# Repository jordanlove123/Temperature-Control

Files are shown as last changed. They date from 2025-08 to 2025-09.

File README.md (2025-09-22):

# Temperature Control
System for controlling temperature of an object to within 10 mK of a given setpoint.

DISCLAIMER: As is discussed below, some parts of the system will have to be designed by the user because they depend on the shape, size, and thermal mass of the object. This means that to a certain extent, performance is dependent on the user's design of these components, but I tried to include as many recommendations as possible for best practices.

## Setup

### Recommended installations
Before starting setup, there is software that is necessary to access some of the files in this repository:
* [Arduino IDE](https://www.arduino.cc/en/software/): Edit and upload Arduino code
* [KiCAD](https://www.kicad.org/download/): View and export PCB files
* [Prusa Slicer](https://www.prusa3d.com/page/prusaslicer_424/): Convert STL 3D models to gcode for a 3D printer
* [Realterm](https://sourceforge.net/projects/realterm/): Send serial commands and save serial data from Arduino to text file

These programs can all be downloaded for free.

### Manufacturing

#### Shield PCB
The PCB files can be found at [Manufacturing/Shield PCB](Manufacturing/ShieldPCB/). In order to get the manufacturing files, open the .kicad_pcb file and export according to what is necessary for your manufacturer of choice. If you don't have a manufacturer of choice, I recommend [JLCPCB](https://jlcpcb.com/). Once you have the board, assemble it according to the component labels in the .kicad_sch file. The complete list of necessary components can be found in the [bill of materials](Manufacturing/BOM.xlsx).

#### Container (optional)
If you have access to a 3D printer, I recommend printing the container found in [Manufacturing/Box](Manufacturing/Box). This can be done by opening the .stl files in Prusa Slicer and converting them to gcode:

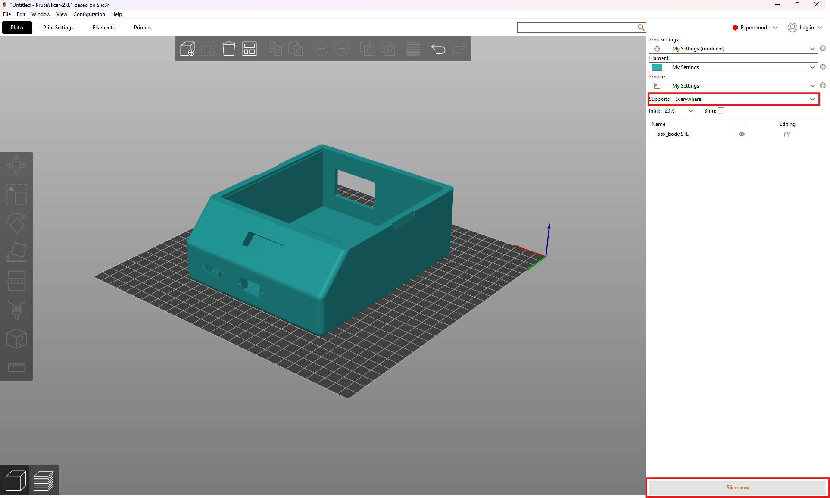
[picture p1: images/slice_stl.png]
Slice .stl file


Then export the gcode file and give it to your 3D printer:

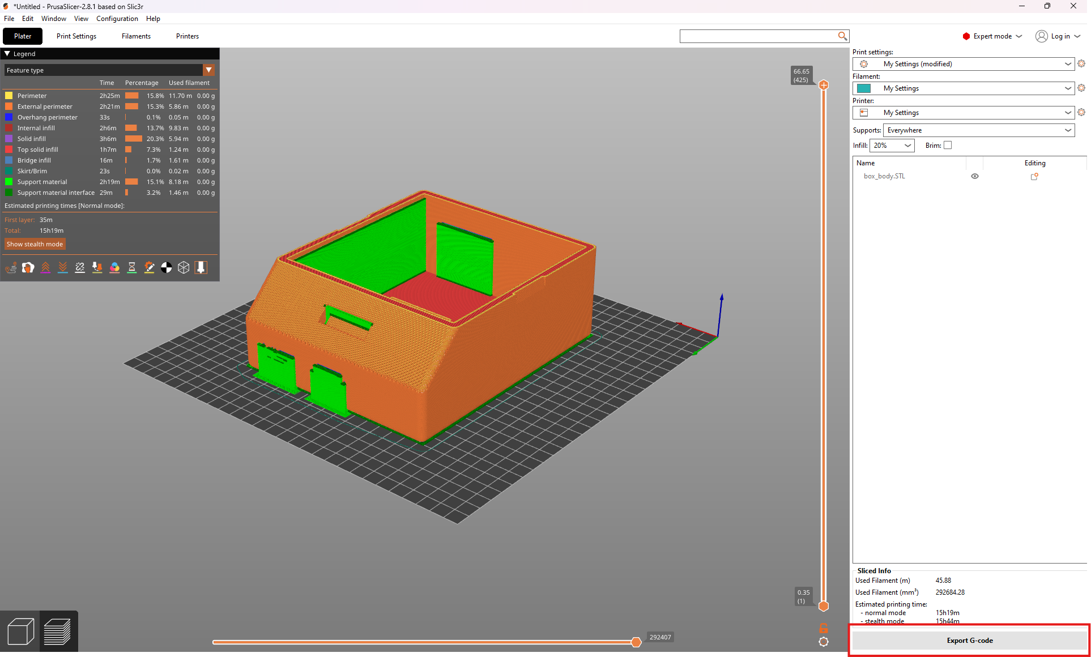
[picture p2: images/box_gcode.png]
Export gcode


#### Temperature Probe
This system uses two temperature sensors: one for the feedback loop that controls the temperature in addition to a heater, and one for independent monitoring of the temperature with a sensor outside the feedback loop. Because the configuration of these sensors and the heater will depend on the form factor of the object being temperature controlled, there is no case for them in this repository, but there are requirements for how it is built. The temperature sensors should be two 10k thermistors in a voltage divider as shown below:

<div align="center">
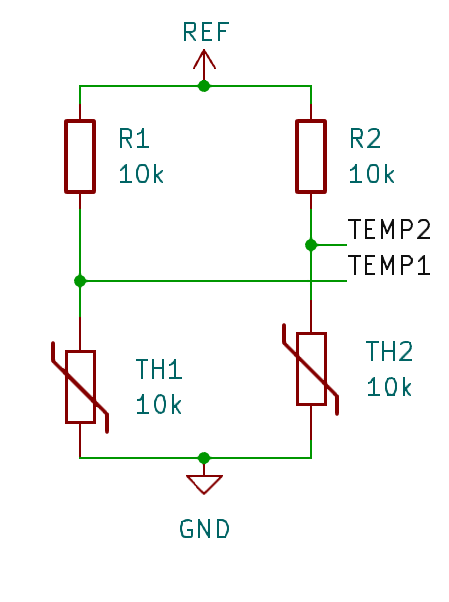
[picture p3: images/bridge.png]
    
</div>

TEMP1 and TEMP2 are the two signal cables that will be connected to IN1 and IN2 on the shield, REF comes from the REF pin on the shield and is generated by the on-board 2.5V voltage regulator, and GND comes from one of the GND pins on the shield. Additionally, a heating resistor connected to the R6 pin header should be placed near the object being temperature controlled. If you're using the optional container, all of the wires in your case should be connected to a d-sub 9 connector so they can be plugged into the container. Some additional recommendations for configuration of the probe:

* Try to thermally isolate the sensor-heater-object system as best as you can with the case that you build. This will have the largest effect on the performance of the system.
* Place the temperature sensors far from the heater. This will ensure that you're measuring the actual temperature of the object, not just the temperature of the heater.
* Don't place the sensors too close to each other so you can see on the independent sensor if the object is being heated unevenly.
* Try to match the resistors in the voltage dividers as best as possible. This will ensure that the voltage you measure on both dividers is the same as long as the temperature is the same.

Because the performance is largely dependent on the probe setup, there are no guarantees that you will get mK-level stability if it isn't good enough. However, below you will find tools to assess the performance and potential flaws of your setup so you can iterate your design until it is good enough.

### Assembly
Connecting the shield PCB to the Arduino is very simple: just align the pins coming from the underside of the PCB with the input pins of the Arduino and connect them directly so the PCB is sitting on top of the Arduino. There should be an exact one-to-one match between PCB pins and Arduino pins. If you're using the optional container, use the following images as a reference to place the components within it correctly.

Box front:

<div align="center">
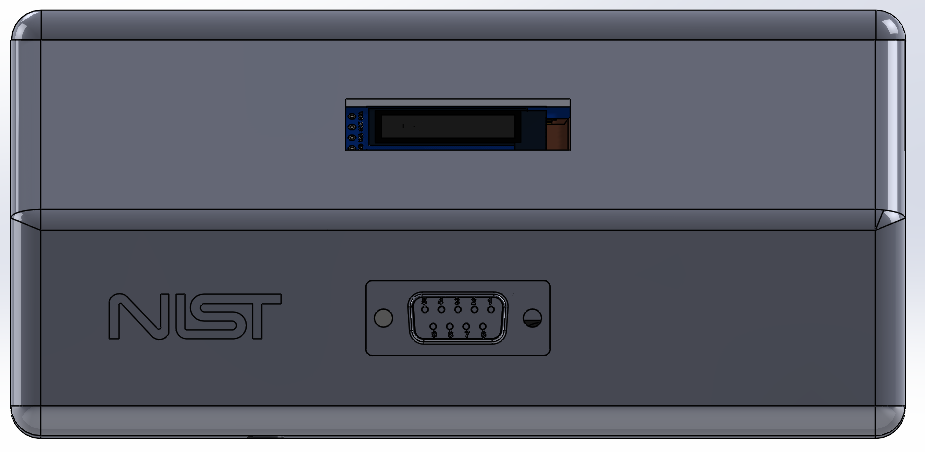
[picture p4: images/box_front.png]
    
</div>

Box back:

<div align="center">
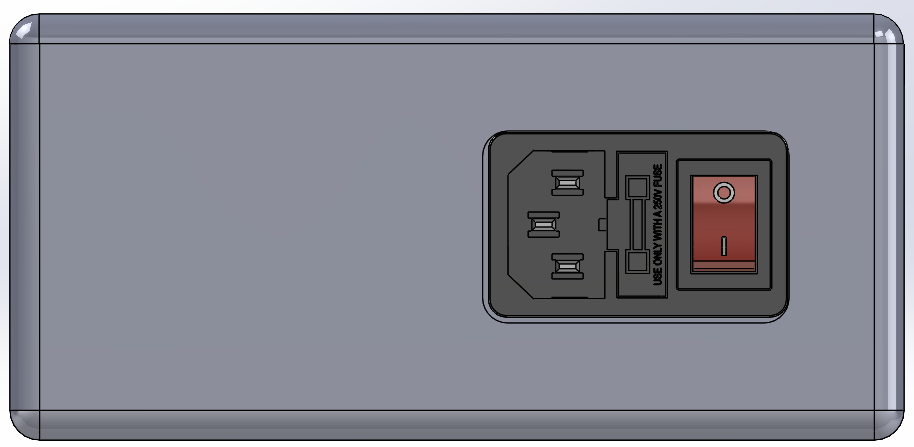
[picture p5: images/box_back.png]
    
</div>

Box top:

<div align="center">
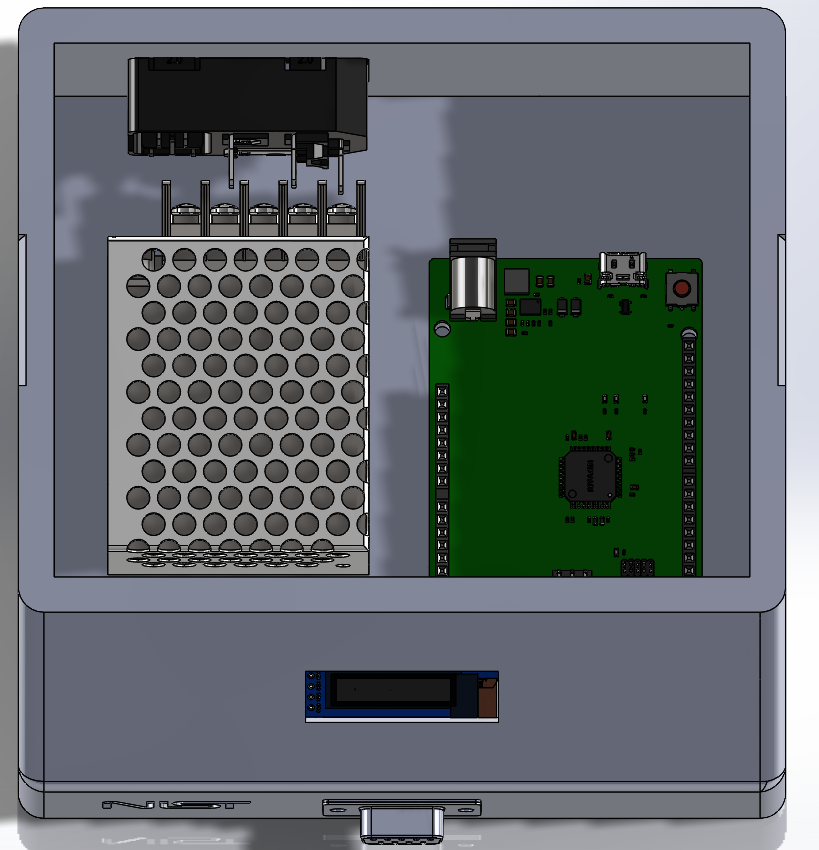
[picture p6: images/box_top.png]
    
</div>

Use the following wiring diagram to make the necessary connections:

<div align="center">
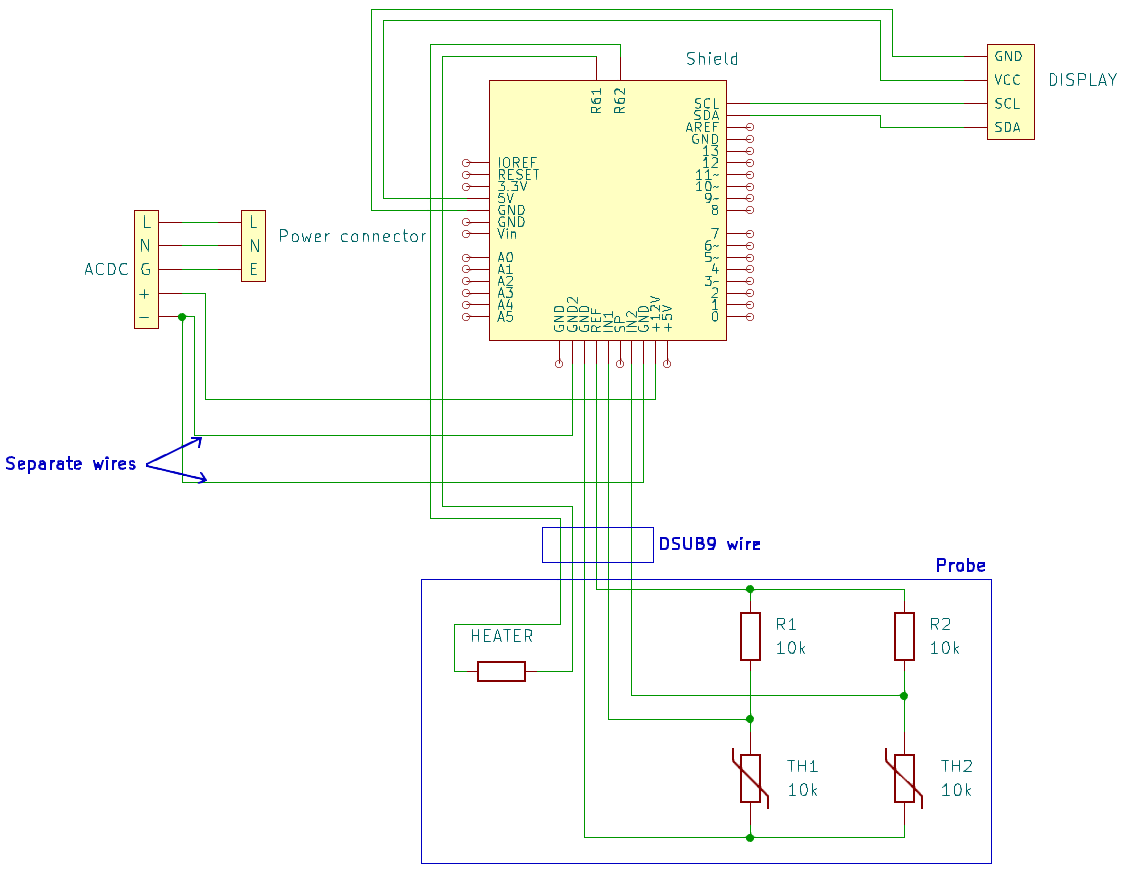
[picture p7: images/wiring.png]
    
</div>

WARNING: THE WALL PLUG CARRIES HIGH VOLTAGES WHEN CONNECTED. BE VERY CAUTIOUS WHEN WORKING WITH POWER CABLES AND DO NOT PLUG IN THE BOX UNTIL ALL THESE CABLES ARE SHRINK WRAPPED AND THERE IS NO EXPOSED METAL. PLUGGING IN WITHOUT TAKING THE CORRECT PRECAUTIONS COULD CAUSE HARM.

### Code
The Arduino code makes use of two custom libraries: AD7190 for interfacing with the ADC on the shield and PID for handling the feedback loop of the system. These two folders can be found in [Code/Libraries](Code/Libraries) and can be installed using the following steps:

* Save both folders as a zip file
* Open the Arduino IDE and select Sketch > Include Library > Add .ZIP Library
* Navigate to the location where your libraries are saved and select them

The code to be uploaded to the Arduino is found in [Code/Arduino](Code/Arduino)

## Usage

### Serial commands
The Arduino accepts a variety of commands to interface with the PID system, which are summarized in the table below:
| Command          | Arguments accepted             | Description                                                                                                 |
|:-----------------|:-------------------------------|:------------------------------------------------------------------------------------------------------------|
| p \[arg1\]       | arg1: double > 0               | Change the K<sub>p</sub> parameter of the PID system                                                        |
| i \[arg1\]       | arg1: double > 0               | Change the K<sub>i</sub> parameter of the PID system                                                        |
| d \[arg1\]       | arg1: double > 0               | Change the K<sub>d</sub> parameter of the PID system                                                        |
| heat \[arg1\]    | arg1: 0 or 1                   | Turn heater off (0) or on (1)<sup>1</sup>                                                                   |
| setp \[arg1\]    | arg1: double < 29              | Change the setpoint of the PID system                                                                       |
| verbose \[arg1\] | arg1: 0 or 1                   | Output control stats to serial port (see [Serial output](#serial-output))                                   |
| rstime           | none                           | Restart the timestamp at 0                                                                                  |
| sint \[arg1\]    | arg1: double                   | Set the integral term to a custom value<sup>2</sup>                                                         |
| save             | none                           | Save the current K<sub>p</sub>, K<sub>i</sub>, K<sub>d</sub>, and setpoint to EEPROM<sup>3</sup>            |

<sup>1</sup> This is implemented in practice by multiplying the heater output by arg1, so passing any other number will have the effect of changing the gain of the entire system

<sup>2</sup> Due to the anti-windup, if |arg1| > 10, it will be set to either -10 or +10

<sup>3</sup> When an Arduio program is running, variables are stored in program memory which is volatile, meaning it is lost when the Arduino loses power. However, the Arduino also has a non-volatile form of data storage called EEPROM, so if you want to move your controller and disconnect power you won't lose the parameters you found during tuning. This memory has a limited number of write cycles though, so use this command sparingly.

Due to an unknown bug in the Arduino code, commands need to be sent multiple times in quick succession in order for them to be properly received.

### Serial output

When verbose is set to true, data is output to the serial port in the following format:

**Timestamp &nbsp;&nbsp;&nbsp; Temperature voltage &nbsp;&nbsp;&nbsp; Independent sensor reading &nbsp;&nbsp;&nbsp; Error voltage &nbsp;&nbsp;&nbsp; Proportional term &nbsp;&nbsp;&nbsp; Integral term &nbsp;&nbsp;&nbsp; Derivative term &nbsp;&nbsp;&nbsp; Output power &nbsp;&nbsp;&nbsp; Output voltage to heater circuit**

### Tuning
DISCLAIMER: This is not necessarily the optimal tuning method, but just the one that I found works best for me. If you have another method that you prefer and you know it works better, go ahead and use it. This is just for a beginner to get a feel for tuning. However, I have found that some common tuning methods don't work very well, possibly because of some of the non-linearities in the system.

NOTE: There is a [jupyter notebook](Code/Data%20Analysis/data_analysis.ipynb) in Code/Data Analysis that can be used to help with tuning. If you would like to use your own analysis techniques, it is not required to use this notebook, however if you have your own analysis techniques in addition to those found in the notebook, you probably don't need this section anyway.

The notebook has 3 main cells that will be useful. The first one, third from the top, will just take your data and plot everything from the serial output on it's own axis for the entire dataset. This can be used to look at your data wholistically and to analyze long term stability. The next cell from the top will plot the last 150 seconds of data, and updates every second. This can be used if you want to see live-updating data and catch any large errors without having to wait to see everything at once. The last one is the PSA spectrum of the P, I, and D terms of the controller and the temperature data. This essentially shows you how much of each frequency is contained in the data, which is useful for reasons explained below.

#### Step response
When tuning, you will want to look at the step response of your system, which is just how it responds to an instantaneous change in the setpoint (In this case, moving it up). Do this by turning off the heater, waiting for the temperature to return to room temperature, then sending the command "sint 0" and turning the heater back on. The step response will be the temperature graph after turning the heat back on.

#### Recognizing issues
Once you get to the point of tuning the parameters of the system, you want to make sure the probe setup is good enough, because otherwise you're limited by the quality of your setup instead of the accuracy of the parameters. The main issue that you will run into with the probe setup is insufficient thermal isolation, which means surrounding air temperature is being factored into your measurement. Generally, the object being temperature controlled will have a much larger thermal mass than the surrounding air, so watch for large, quick changes in temperature. A normal time period for a temperature change depends on your thermal mass, but will typically be on the order of a couple minutes. If you see relatively large temperature changes happening in a matter of seconds, it's probably a probe issue rather than a parameter issue.

#### Step 0: The basics
Before starting, a general overview of PID. PID stands for proportional, integral, derivative, and controls a system using exactly those things. It takes as input the error between the setpoint and the actual temperature and outputs the negative sum of the integral of the error, derivative of the error, and exact error all scaled by constants, called the gains. The proportional term just pushes the temperature towards the setpoint. This might be enough in some cases, but think about what would happen if the error were 0 and the temperature was above room temperature. A controller with only the proportional term would not be doing anything to keep the temperature above room temperature because K*0 = 0 so it would output 0. This means any controller with only the proportional term will have some steady state error. This is where the integral term comes in. If there is any steady state error, the integral term will accumulate over time, pushing the temperature towards the setpoint. The speed that it accumulates is dictated by the integral gain. Notably, too high of a proportional gain or integral gain will cause oscillations, which are not what we want. This is where the derivative term comes in. It can be thought of as predicting the future; if the derivative is positive, the temperature will probably go up, and so the derivative term preemptively reduces the output power to reduce this change. Such a term will provide damping of oscillations, and that is its job.

#### Step 1: Picking a setpoint
Before doing any tuning, figure out the ambient temperature of the object being temperature controlled using the system. The system guarantees high precision, but not high accuracy, so doing this will give you a frame of reference for what the temperature actually is. Once you've done this, set the setpoint. It can be whatever you want but is bounded on both sides by two factors: the bottom end is about 2-3 <sup>o</sup>C above room temperature since the system has no cooler so ambient temperature is used to cool it, and the upper end is limited by your heater's power output. This depends on the resistance of the heater and the input voltage that you use (12V if you use the optional container with no modifications).

#### Step 2: Finding proportional gain
The next step after setting the setpoint is to find K<sub>p</sub>, the proportional gain of the system. To find the proportional gain, just pick a number to start. If the step response goes past the setpoint, reduce it by half until it doesn't. Then, slowly turn it up and watch the step response each time you change it. Once it is settling close to the setpoint, but slightly below, move on to step 3.

#### Step 3: Finding integral gain
First, cut your proportional gain in half, and then pick a number for your integral gain. It will probably be much smaller than the proportional gain you found. If the oscillations are centered above the setpoint while it settles, turn the integral gain down. If below, do the opposite. Once the oscillations are centered approximately at the setpoint, move on to the next step.

#### Step 4: Finding derivative gain
This step is pretty simple, just turn up the derivative gain until the oscillations are damped as much as is necessary for your purposes. The higher it is, the more damped they will be. If your derivative gain gets too high, the integral term might accumulate more than it was before because the derivative term slows the original ascent to the setpoint, so you'll need to turn down the integral gain slightly. Once you've finished finding the parameters, a good step response will look something like this:

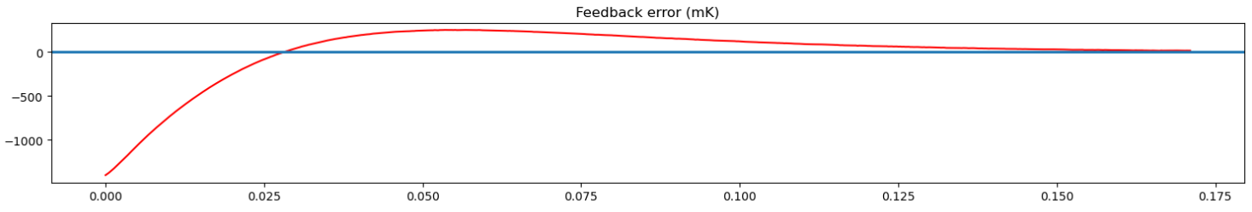
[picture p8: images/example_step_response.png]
Example step response


#### Step 5: Fine tuning the parameters
The above steps help with the original settling to the setpoint, but in order to get the best steady state performance, the parameters need to be tuned a little more. To do this, take about 12 hours of data after the temperature has settled and look at the PSA spectrum. An ideal spectrum will look like this:

<div align="center">
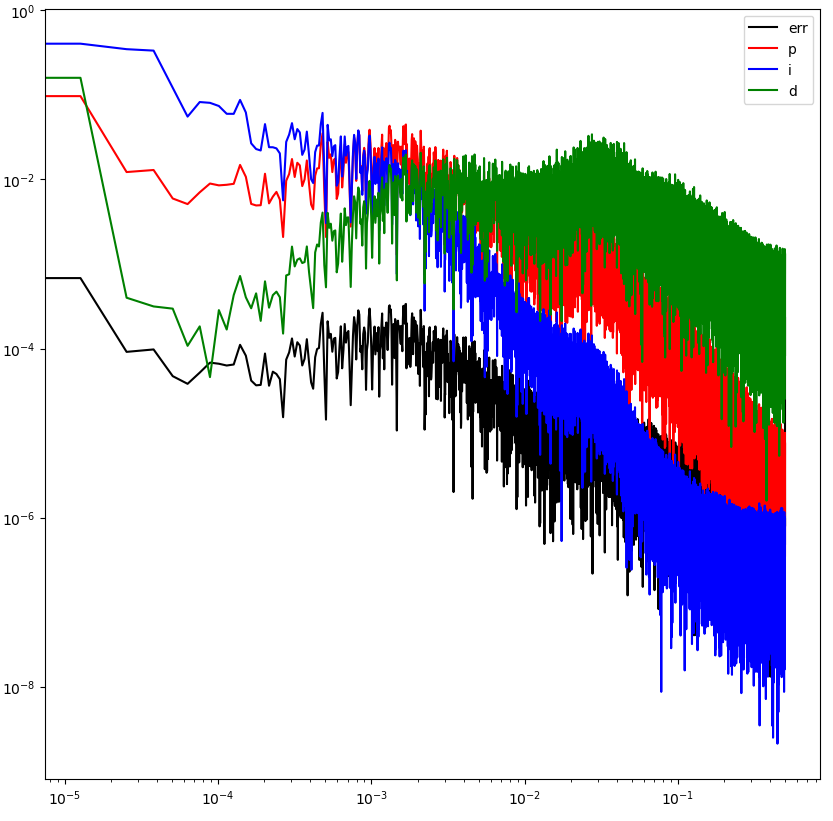
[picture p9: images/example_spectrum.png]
    
</div>

Note the integral term is the strongest at lower frequencies, then the proportional term takes over in the middle frequencies, and finally the derivative term takes over at high frequencies. It will also have two points where all terms will start to roll off: one is the natural frequency of your system; the temperature can't change any faster than that, and the other is due to a filter in the feedback loop. Just ignore these and look at the general shape. If the shape doesn't look like this, you can move each term up by multiplying it by a scaling factor, and move it down by dividing by a scaling factor. Scale the parameters appropriately and they should then be optimal.

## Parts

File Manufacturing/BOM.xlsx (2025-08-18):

Item | Digikey part number | Price | Quantity | Total Price | Optional?
Shield header kit | 1568-11417-ND | $2.75 | 1 | $2.75 | n
Fuse | 283-3263-ND | $0.91 | 1 | $0.91 | y
Schottky Diode | 1N5819HW-FDICT-ND | $0.23 | 1 | $0.23 | n
Inductor 330u | 495-B82432C1334K000CT-ND | $5.86 | 1 | $5.86 | n
Capacitor 330u | 478-APA0609331M010RCT-ND | $0.54 | 1 | $0.54 | n
Buck Converter | LM2575D2T-5R4GOSCT-ND | $17.92 | 1 | $17.92 | n
2 pin header | 952-2262-ND | $0.79 | 1 | $0.79 | n
Resistor 1k | 541-1.00KCCT-ND | $0.10 | 4 | $0.40 | n
Resistor 10k | RMCF0805FT10K0CT-ND | $0.10 | 1 | $0.10 | n
Resistor 10 | P10.0CCT-ND | $0.11 | 1 | $0.11 | n
Capacitor 1u | 1276-1029-1-ND | $0.08 | 5 | $0.40 | n
Resistor 5k | 541-CRCW08055K00FKTACT-ND | $0.11 | 1 | $0.11 | n
MMBT3904 Transistor | 4878-MMBT3904CT-ND | $0.11 | 1 | $0.11 | n
2.5 Vref | 296-39165-1-ND | $3.54 | 1 | $3.54 | n
AD7190 ADC | 505-AD7190BRUZ-REELCT-ND | $18.14 | 1 | $18.14 | n
Arduino uno r4 minima | 1050-ABX00080-ND | $20.00 | 1 | $20.00 | n
D-sub 9 connector | AE11063-ND | $0.52 | 2 | $1.04 | y
D-sub 9 cable | 116-30-9506-99-ND | $4.71 | 1 | $4.71 | y
Power cable | TL870-ND | $12.56 | 1 | $12.56 | y
ACDC converter | 1866-4128-ND | $8.60 | 1 | $8.60 | y
Jumper wires | 4526-KIT-ZW-20X3-ND | $14.80 | 1 | $14.80 | n
Power receptacle | 2057-IEC-GS-1-100-ND | $5.31 | 1 | $5.31 | y
Thermistor | 317-1258-ND | $0.32 | 2 | $0.64 | n
THT resistor 10k | CF14JT10K0CT-ND | $0.10 | 2 | $0.20 | n
Heating resistor | A129453CT-ND | $0.56 | 1 | $0.56 | n
OLED display* | etsy (https://www.etsy.com/listing/1593848368/128x32-oled-lcd-display-ssd1306-driver?gpla=1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) | $6.99 | 1 | $6.99 | y
PCB* | jlcpcb (https://jlcpcb.com/) | $20.00 | 1 | $20.00 | n
 |  |  | Total | $147.32
*Item not on digikey |  |  | Total without optional | $107.20

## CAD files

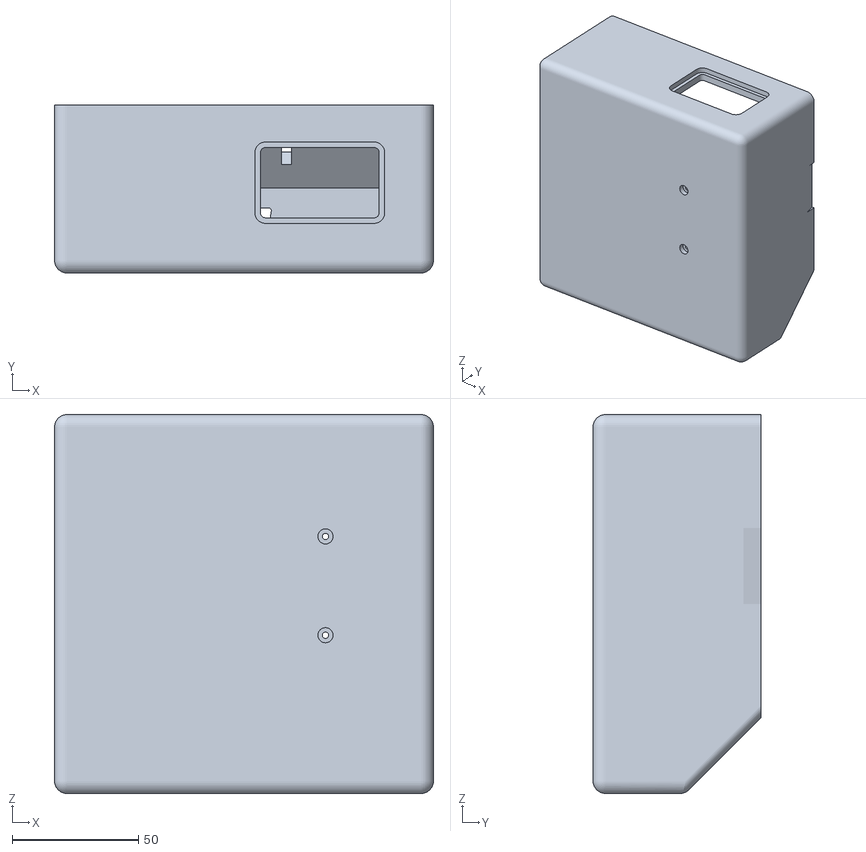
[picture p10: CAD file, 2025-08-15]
Manufacturing/Box/box_body.STL
150.0 x 66.5 x 150.0

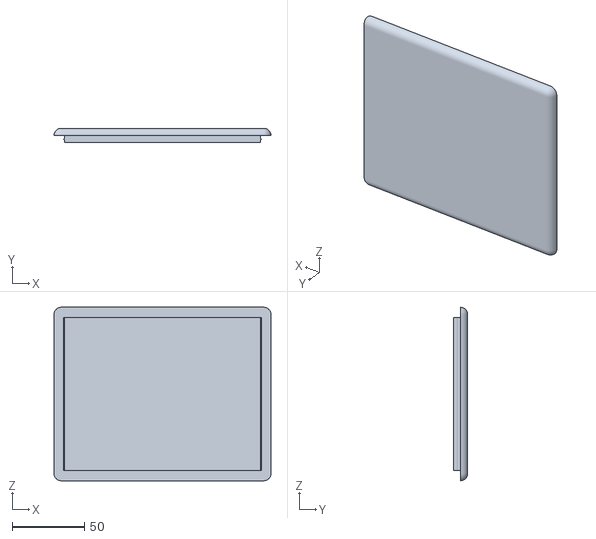
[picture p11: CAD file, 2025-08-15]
Manufacturing/Box/box_top.STL
150.0 x 10.0 x 120.0

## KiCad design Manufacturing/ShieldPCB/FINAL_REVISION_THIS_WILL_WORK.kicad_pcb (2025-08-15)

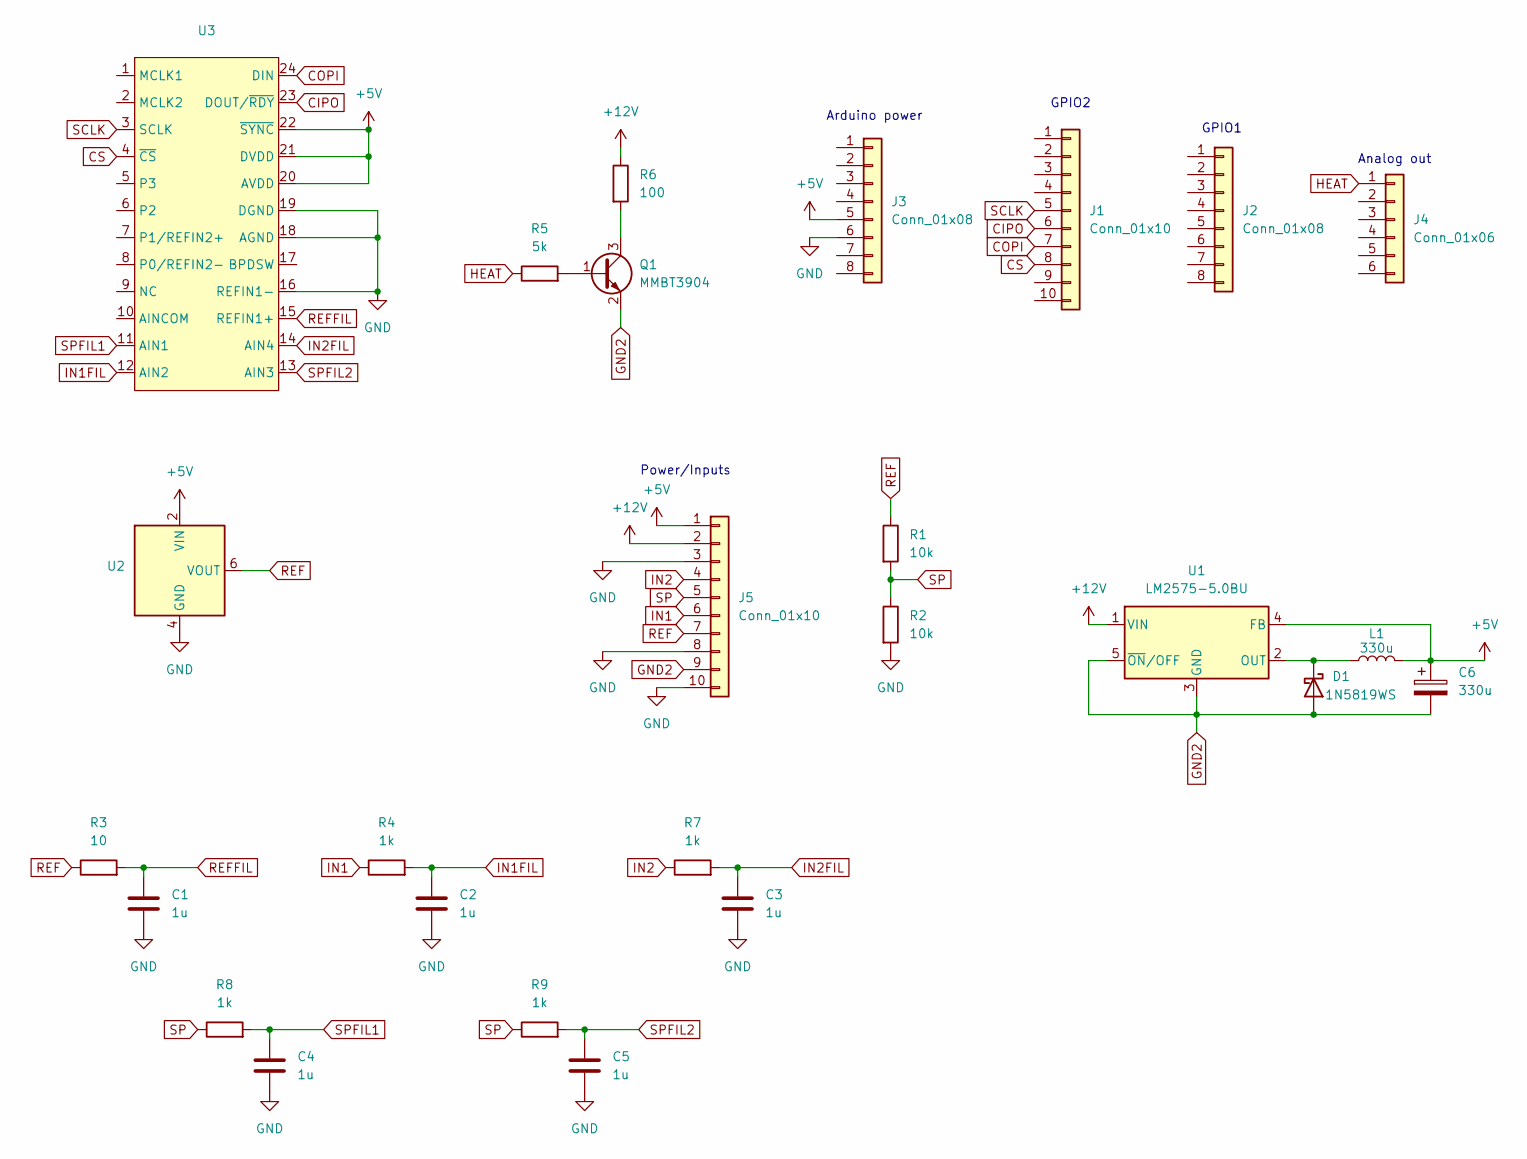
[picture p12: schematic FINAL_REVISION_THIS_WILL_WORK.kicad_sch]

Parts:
C1, C2, C3, C4, C5: 1u; C_0805_2012Metric
C6: 330u; C_Elec_6.3x7.7
D1: 1N5819WS; D_SOD-123
J1: Conn_01x10; PinSocket_1x10_P2.54mm_Vertical
J2, J3: Conn_01x08; PinSocket_1x08_P2.54mm_Vertical
J4: Conn_01x06; PinSocket_1x06_P2.54mm_Vertical
J5: Conn_01x10; PinHeader_1x10_P2.54mm_Vertical
L1: 330u; L_1812_4532Metric
Q1: MMBT3904; SOT-23
R1, R2: 10k; R_0805_2012Metric
R3: 10; R_0805_2012Metric
R4, R7, R8, R9: 1k; R_0805_2012Metric
R5: 5k; R_0805_2012Metric
R6: 100; PinHeader_1x02_P2.54mm_Vertical
U1: LM2575-5.0BU; TO-263-5_TabPin3
U2: SOIC-8_3.9x4.9mm_P1.27mm
U3: TSSOP-24_4.4x7.8mm_P0.65mm

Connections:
+5V: C6.1, J3.5, J5.1, L1.2, U1.4 (FB), U2.2 (VIN), U3.20 (AVDD), U3.21 (DVDD), U3.22 (~SYNC)
+12V: J5.2, R6.1, U1.1 (VIN)
CIPO: J1.6, U3.23 (DOUT/~RDY)
COPI: J1.7, U3.24 (DIN)
CS: J1.8, U3.4 (~CS)
GND: C1.2, C2.2, C3.2, C4.2, C5.2, J3.6, J5.3, J5.8, J5.10, R2.2, U2.4 (GND), U3.16 (REFIN1-), U3.18 (AGND), U3.19 (DGND)
GND2: C6.2, D1.2 (A), J5.9, Q1.2 (E), U1.3 (GND), U1.5 (~ON/OFF)
HEAT: J4.1, R5.1
IN1: J5.6, R4.1
IN1FIL: C2.1, R4.2, U3.12 (AIN2)
IN2: J5.4, R7.1
IN2FIL: C3.1, R7.2, U3.14 (AIN4)
unnamed: D1.1 (K), L1.1, U1.2 (OUT)
unnamed: Q1.1 (B), R5.2
unnamed: Q1.3 (C), R6.2
REF: J5.7, R1.1, R3.1, U2.6 (VOUT)
REFFIL: C1.1, R3.2, U3.15 (REFIN1+)
SCLK: J1.5, U3.3 (SCLK)
SP: J5.5, R1.2, R2.1, R8.1, R9.1
SPFIL1: C4.1, R8.2, U3.11 (AIN1)
SPFIL2: C5.1, R9.2, U3.13 (AIN3)

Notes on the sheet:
Arduino power
GPIO2
GPIO1
Analog out
Power/Inputs

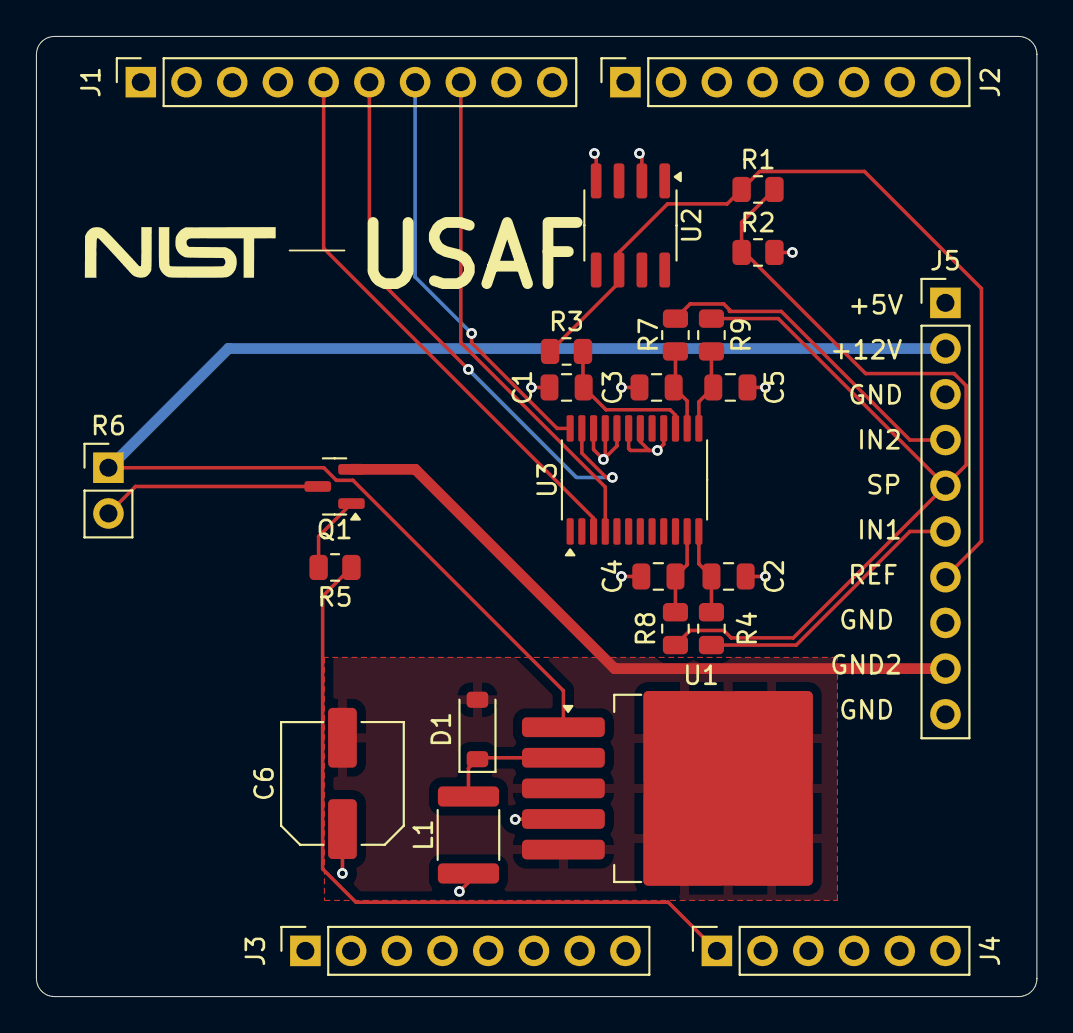
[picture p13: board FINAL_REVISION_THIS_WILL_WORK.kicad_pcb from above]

Board: 4 copper layers, 55.6 x 53.3 mm, 26 parts (0 on the bottom side), 21 nets.

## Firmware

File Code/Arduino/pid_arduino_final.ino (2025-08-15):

#include <SPI.h>
#include <Wire.h>
#include <Adafruit_GFX.h>
#include <Adafruit_SSD1306.h>
#include <AD7190.h>
#include <PID.h>
#include <math.h>
#include <EEPROM.h>

#define CS 10

#define SCREEN_WIDTH 128 // OLED display width, in pixels
#define SCREEN_HEIGHT 32 // OLED display height, in pixels
#define OLED_RESET     -1 // Reset pin # (or -1 if sharing Arduino reset pin)
#define SCREEN_ADDRESS 0x3C ///< See datasheet for Address; 0x3D for 128x64, 0x3C for 128x32
Adafruit_SSD1306 display(SCREEN_WIDTH, SCREEN_HEIGHT, &Wire, OLED_RESET);

// Display data
byte curr_ind = 0;
byte low[128];
byte high[128];
double max_candidate = -4;
double min_candidate = 4;

AD7190 ad7190(2.495);
//      130, 0.685, 5400
PID pid(130, 0.685, 5400, 0.00825, 120, true);
String c;
String in;
char buf1[16];
char buf2[16];
const double A = 0.001125308852122;
const double B = 0.000234711863267;
const double C = 0.000000085663516;
double vcc = 2.5;
int count = 0;
double sp_off = -0.05;
double last_params[4] = {0, 0, 0, 0};
double params_buf[4];

void double_to_eeprom(double d, int start_addr) {
  double *d_ptr = &d;
  long long d_int = *((long long*) d_ptr);
  byte temp;
  for (int i = 7; i >= 0; i--) {
    temp = (d_int >> (i*8)) & 0xFF;
    EEPROM.write(start_addr + 7-i, temp);
  }
}

double double_from_eeprom(int start_addr) {
  long long buf = 0;
  for (int i = 0; i < 8; i++) {
    long long temp = EEPROM.read(start_addr + i);
    buf |= temp << (7-i)*8;
  }
  long long *buf_ptr = &buf;
  double d = *((double*) buf_ptr);
  return d;
}

void load_params(double *buf) {
  // [sp, p, i, d]
  // !!!! Can cause buffer overflow if len(buf) < 4, don't do that !!!!
  for (int i = 0; i < 4; i++) {
    double temp = double_from_eeprom(8*i);
    if (isnan(temp) && i == 0) {
      temp = 27.5;
    }
    else if (isnan(temp)) {
      temp = 1;
    }
    buf[i] = temp;
  }
}

void save_params(double *params) {
  // !!!! len(params) must be 4 for correct operation !!!!
  for (int i = 0; i < 4; i++) {
    if (last_params[i] != params[i]) {
      last_params[i] = params[i];
      double_to_eeprom(params[i], 8*i);
    }
  }
}

double t_to_r(double T) {
  double x = 1/C*(A-1/(T+273.15));
  double y = sqrt(pow(B/(3*C), 3) + pow(x/2, 2));
  return exp(cbrt(y-x/2) - cbrt(y+x/2));
}

double r_to_v(double R) {
  return vcc * R / (10000 + R);
}

void updateDisplay(byte *low, byte *high, int curr_ind) {
  display.clearDisplay();
  int start = (curr_ind + 1) % 128;
  for (int i = 0; i < 128; i++) {
    for (int j = low[(i + start) % 128]; j <= high[(i + start) % 128]; j++) {
      display.drawPixel(i, j, SSD1306_WHITE);
    }
  }
  display.display();
}

void updateParams() {
  c = Serial.readStringUntil(' ');
  in = Serial.readStringUntil('\n');
  if (c != NULL && in != NULL) {
    c.toCharArray(buf1, 16);
    in.toCharArray(buf2, 16);
    int setting = atof(buf2);
    if (strcmp(buf1, "p") == 0) {
      pid.K_p = setting;
      params_buf[1] = setting;
    }
    else if (strcmp(buf1, "i") == 0) {
      pid.K_i = setting;
      params_buf[2] = setting;
    }
    else if (strcmp(buf1, "d") == 0) {
      pid.K_d = setting;
      params_buf[3] = setting;
    }
    else if (strcmp(buf1, "heat") == 0) {
      pid.heat = setting;
    }
    else if (strcmp(buf1, "setp") == 0) {
      sp_off = r_to_v(t_to_r(setting)) - 1.181;
      params_buf[0] = setting;
    }
    else if (strcmp(buf1, "verbose") == 0) {
      pid.verbose = setting;
    }
    else if (strcmp(buf1, "sint") == 0) {
      pid.set_integral(setting);
    }
  }
  else if (in != NULL) {
    in.toCharArray(buf1, 16);
    if (strcmp(buf1, "rstime") == 0) {
      pid.set_start_time();
    }
    else if (strcmp(buf1, "save") == 0) {
      save_params(params_buf);
    }
  }
}

void setup()
{
  Serial.begin(9600);
  analogWriteResolution(12);
  Serial.setTimeout(2);
  display.begin(SSD1306_SWITCHCAPVCC, SCREEN_ADDRESS);

  // Select ADC
  pinMode(CS, OUTPUT);
  digitalWrite(CS, LOW);

  // Initialize ADC and PID
  ad7190.init(AD7190::AIN2_2);
  pid.set_start_time();

  // Retrieve parameters from EEPROM
  load_params(params_buf);
  sp_off = r_to_v(t_to_r(params_buf[0])) - 1.181;
  pid.K_p = params_buf[1];
  pid.K_i = params_buf[2];
  pid.K_d = params_buf[3];

  // Set up display buffers
  for (int i = 0; i < 128; i++) {
    low[i] = 16;
    high[i] = 16;
  }
  updateDisplay(low, high, 0);
}

void loop() {
  double temp_v = 1.185 - ad7190.read_data(AD7190::AIN1_2);
  updateParams();
  double err = ad7190.read_data(AD7190::AIN3_4) + sp_off;

  double temp_err = 37.1*err*1000;
  if (temp_err > max_candidate) {
    max_candidate = temp_err;
  }
  if (temp_err < min_candidate) {
    min_candidate = temp_err;
  }
  count++;
  if (count == 150*120) {
    low[curr_ind] = (1-(max_candidate+3.0)/6.0)*32.0;
    high[curr_ind] = (1-(min_candidate+3.0)/6.0)*32.0;
    updateDisplay(low, high, curr_ind);
    curr_ind = (curr_ind + 1) % 128;
    count = 0;
    min_candidate = 4;
    max_candidate = -4;
  }
  pid.pid(temp_v, err);
  updateParams();
}
